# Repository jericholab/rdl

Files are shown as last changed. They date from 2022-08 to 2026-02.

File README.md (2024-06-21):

# Resistance Data Logger (RDL) by Jericho Lab

The RDL is an open-source suite of ready-to-use data logger and sensors designed for scientists and engineers.

The RDL is an open-source ready-to-use data logger designed for scientists and engineers.

For bugs and suggestions, users are invited to submit issues via Github.

Visit the official website: https://jericholab.com

**Purchase orders**  
Contact us via email or Linkedin.
 
**Licenses**  
SOFTWARE: GPL 3.0 license  
HARDWARE: MIT license  
WEBSITE & DOCUMENTS: Creative Commons CC-BY-NC-SA (Non-commercial use only)

For more information about the user permissions and responsibilities associated with each license, please refer to our website or contact us via email at info@jericholab.com. Thank you! 

<figure>
<p align="center">
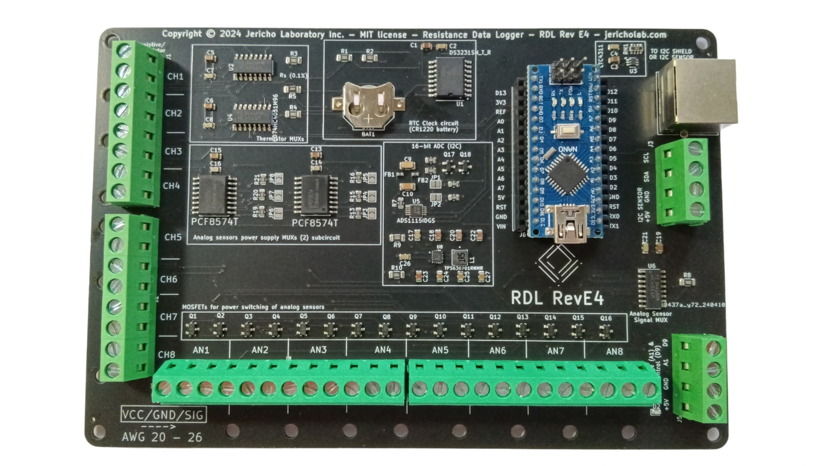
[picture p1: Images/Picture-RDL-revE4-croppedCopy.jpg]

  </p>
<p align="center">
RDL Data Logger revE4 with two I2C Shields
  </p>
</figure>

<figure>
<p align="center">
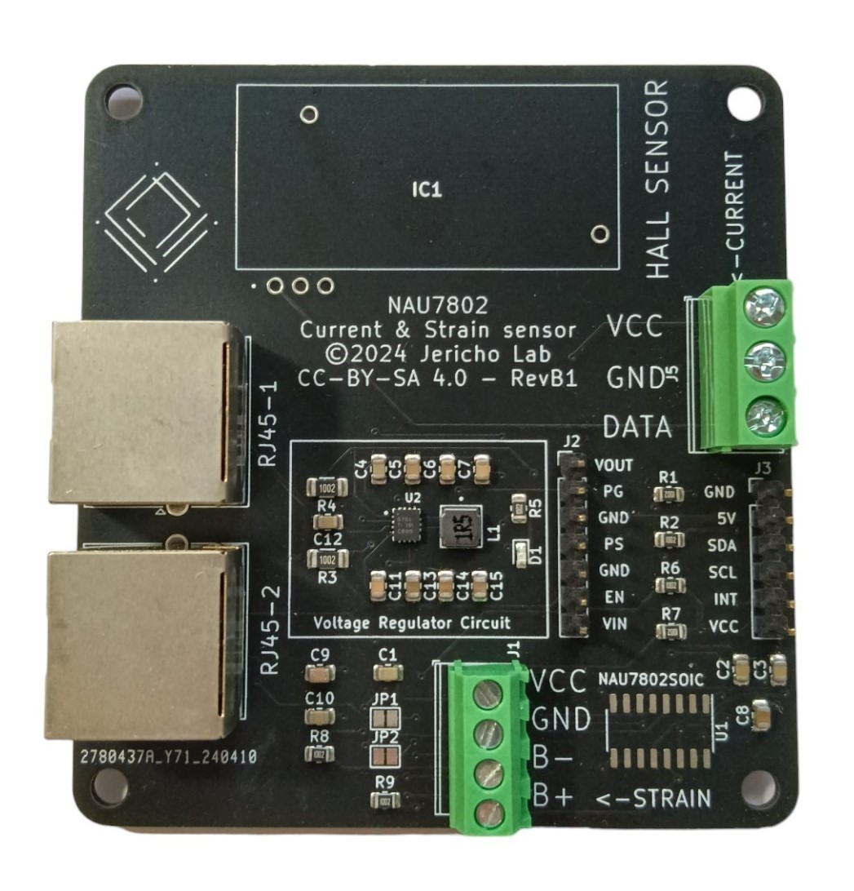
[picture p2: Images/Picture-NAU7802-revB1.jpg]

  </p>
<p align="center">
NAU7802 RevB1 for strain, force and current measurements
  </p>
</figure>

<figure>
<p align="center">
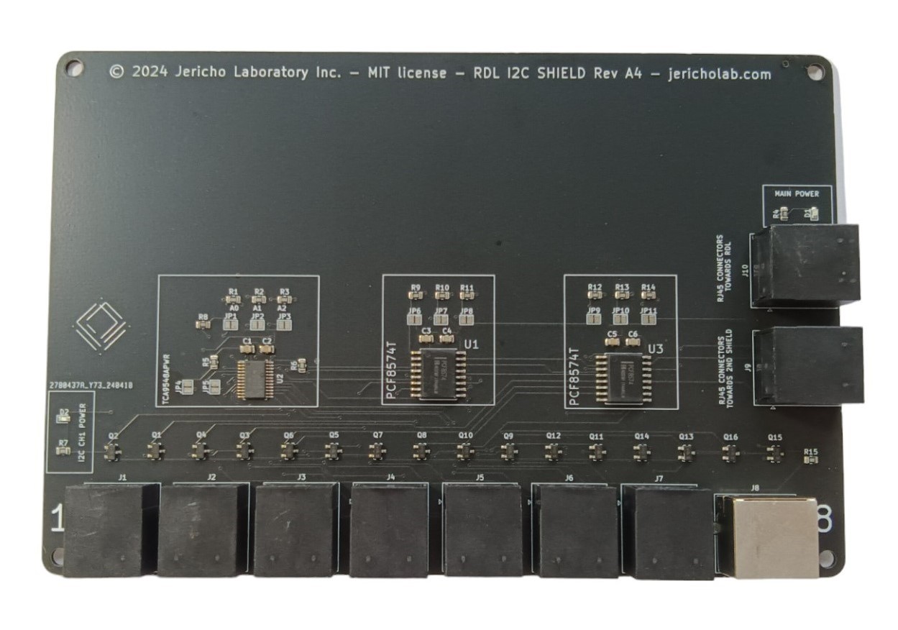
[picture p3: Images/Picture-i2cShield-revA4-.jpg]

  </p>
<p align="center">
RDL I2C Shield, revA4
  </p>
</figure>

<figure>
<p align="center">
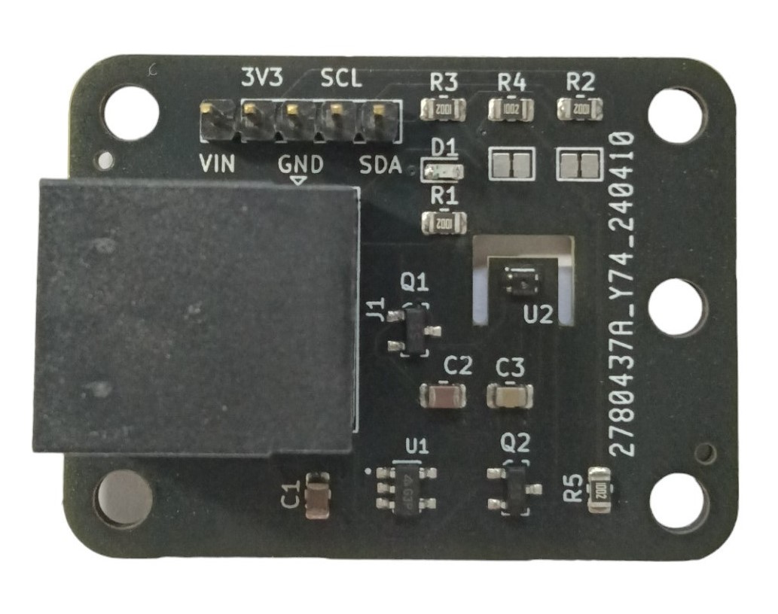
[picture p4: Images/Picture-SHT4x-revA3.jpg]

  </p>
<p align="center">
SHT4X revA4 for temperature and air humidity measurements
  </p>
</figure>

<figure>
<p align="center">
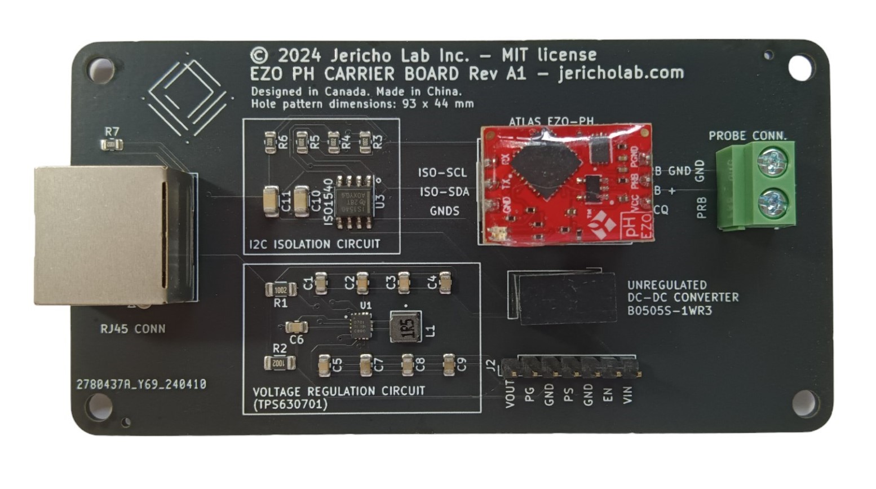
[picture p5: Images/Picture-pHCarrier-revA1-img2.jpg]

  </p>
<p align="center">
Carrier board for EZO PH (Atlas Scientific), revA1
  </p>
</figure>

<figure>
<p align="center">
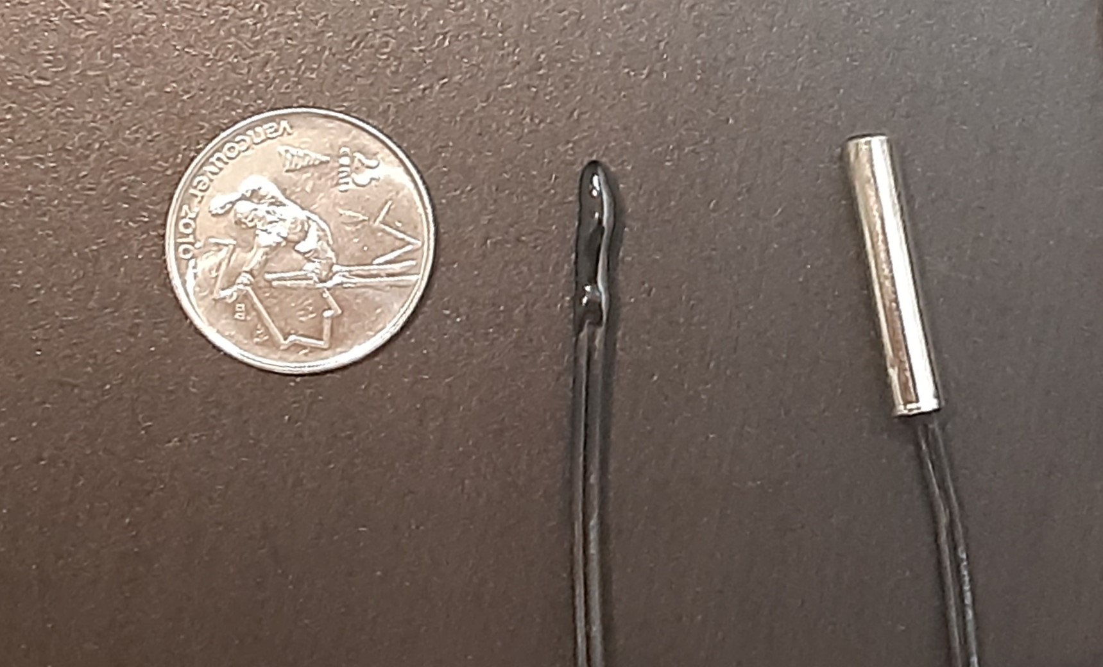
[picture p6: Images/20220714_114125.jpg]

  </p>
<p align="center">
NTC Thermistor probes TH-1 and TH-2 for temperature measurements
  </p>
</figure>

<figure>
<p align="center">
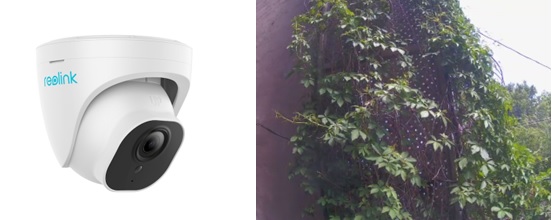
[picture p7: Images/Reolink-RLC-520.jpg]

  </p>
<p align="center">
 Python controlled Reolink RLC-520A Surveillance camera
  </p>
</figure>

<figure>
<p align="center">
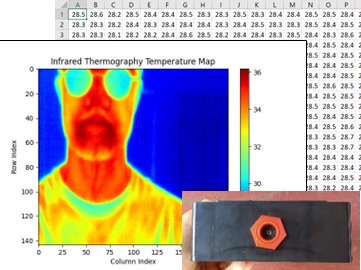
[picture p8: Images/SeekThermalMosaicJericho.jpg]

  </p>
<p align="center">
Outdoor radiographic camera based on Seek Thermal Mosaic Core
  </p>
</figure>

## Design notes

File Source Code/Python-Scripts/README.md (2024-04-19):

PYTHON SCRIPTS

The python scripts allow the integration of the surveillance camera, the infrared camera and the RDL Data Logger into the Orange Pi 4 LTS. The Python scripts can be run in various ways:
1) Run a single script within Thonny
2) Run all scripts by executing the shell script "WIRED-runAll.sh"
3) Run them via Daemons (next section)

DAEMONS

A shell script (.sh) will activate permanent services (daemons) via configuration files (.services) which run the usual python scripts (e.g. infrared.py).

1- Stop all the WIRED python scripts, if any were running.

2- Open a new terminal in the "/daemons-wired "folder, and execute  "$ sudo ./wired-enable-start-all-daemons.sh". This will copy a few files into the system, enable the daemons, start the scripts and show status.

3- You can verify the scripts are running by verifying the usual output (/logging-folder).

4- If you only want to verify that each python script is running, open a terminal in the "/daemons-wired "folder, and execute  "$ sudo ./wired-status-daemons.sh". Use page up and page down to look at all the lines.

5- Reboot the computer and verify the scripts are still running (since the daemons have been enable, they will start at boot time)

6- If you want to stop and disable all the scripts, execute  "$ sudo ./wired-disable-stop-all-daemons.sh"

7- If you wish to stop temporarily a given script (e.g. infrared camera), "$ systemctl stop infrared.service"  (It WILL restart at next OS reboot)

8- If you wish to stop permanently a given script (e.g. infrared camera), "$ systemctl disable infrared.service"  (It WILL NOT restart at next OS reboot)

Remember to keep the files associated with daemons in their own subfolder.

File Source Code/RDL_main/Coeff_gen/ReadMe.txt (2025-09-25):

1. Go to "Source Code/Coeff_gen/" and execute the RunMe.py script file. This will generate a header file (i.e. coefficients.h).
2. Copy coefficients.h to "../RDL_main/Coeff_gen/"
3. Compile RDL_main with the Arduino IDE compiler function.

END

the Jericho Lab team

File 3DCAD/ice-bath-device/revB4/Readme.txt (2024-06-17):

ice-bath-device-revB4

------ List of successful 3D Printing material
OVERTURE PETG Filament 1.75mm

------ 3D Printing Software version used 
Ultimaker Cura 5.2.1

------ Printing profile
N/A. As a starting point, the standard Jericho profile can be used (Profile-PETG-Bibo2-extruder-no2-2024-04-18.curaprofile).

------ 3D Printing Machine Used
Bibo 2

------ Reference to original design, if applicable 
Original design by Jericho Lab, copyright applies, open-source license CC-BY-NC-SA

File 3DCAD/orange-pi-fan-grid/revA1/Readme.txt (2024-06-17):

orange-pi-fan-grid-revA1

------ List of successful 3D Printing material
OVERTURE PETG Filament 1.75mm
PLA Filament 1.75mm

------ 3D Printing Software version used 
Ultimaker Cura 5.2.1

------ 3D Printing Machine Used
Bibo 2

------ Reference to original design, if applicable 
Original design by Jericho Lab, copyright applies, open-source license CC-BY-NC-SA

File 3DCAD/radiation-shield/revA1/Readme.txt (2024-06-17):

radiation-shield-adapter-revA1

------ Radiation shield adapter for the Jericho SHT4X board
Other parts of the Open Source Radiation Shield design included for reference only (Plates, topPlate,pipeSupport, SensorSupport)

------ List of successful 3D Printing material
OVERTURE PETG Filament 1.75mm

------ 3D Printing Software version used 
Ultimaker Cura 5.2.1

------ 3D Printing Machine Used
Bibo 2

------ Reference to original design, if applicable 
Original design by FAST Research group, available on appropedia.org.
https://www.appropedia.org/Design_and_Implementation_of_3-D_Printed_Radiation_Shields_for_Environmental_Sensors
Modifications by Jericho Lab, copyright applies, open-source license CC-BY-NC-SA

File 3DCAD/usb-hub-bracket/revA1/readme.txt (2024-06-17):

usb-hub-bracket-revA

------ Description
Allow the installation of USB hub to mounting panel. Design adapted model "Atolla Aluminum 4-in-1 USB Splitter with 1 USB 3.0 Port and 3 USB 2.0 Ports"

------ List of successful 3D Printing material
OVERTURE PETG Filament 1.75mm

------ 3D Printing Software version used 
Ultimaker Cura 5.2.1

------ 3D Printing Machine Used
Bibo 2

------ Reference to original design, if applicable 
Original design by Jericho Lab, copyright applies, open-source license CC-BY-NC-SA

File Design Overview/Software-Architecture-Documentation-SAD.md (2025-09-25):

**Software Architecture Documentation (SAD) for RDL**  
=======================================
Copyright: Jericho Laboratory Inc.  
Documentation license: CC-BY-SA.  

# Table of Contents

- [Introduction](#introduction)
- [High-Level Flow Diagram](#high-level-flow-diagram)
- [General Ideas](#general-ideas)
- [Fundamental Concepts](#fundamental-concepts)
- [Included Libraries](#included-libraries)
- [Main Code](#main-code)
  - [Declarations](#declarations)
  - [Setup()](#setup)
  - [Loop()](#loop)
- [Main Functions](#main-functions)
  - [ControlFunc()](#controlfunc)
  - [currentNAU7802()](#currentnau7802)
  - [initRTC()](#initrtc)
  - [phFunc()](#phfunc)
  - [printHeader()](#printheader)
  - [runRTC()](#runrtc)
  - [SHT40Func()](#sht40func)
  - [simpleVoltFunc()](#simplevoltfunc)
  - [startMessage()](#startmessage)
  - [strainFunc()](#strainfunc)
  - [terosFunc()](#terosfunc)
  - [thermistor()](#thermistor)
- [Support Functions](#support-functions)
  - [ADS1115.begin()](#ads1115begin)
  - [blink()](#blink)
  - [calculatePhi()](#calculatephi)
  - [commands()](#commands)
  - [getI2Cfreq()](#geti2cfreq)
  - [getVoltFunc()](#getvoltfunc)
  - [i2cScan()](#i2cscan)
  - [I2CSelect()](#i2cselect)
  - [isDST()](#isdst)
  - [pcf1.begin()](#pcf1begin)
  - [readEEPROM()](#readeeprom)
  - [resetFunc()](#resetfunc)
  - [setMultiplexer()](#setmultiplexer)
  - [setTime()](#settime)
  - [spacing1()](#spacing1)
  - [spacing2()](#spacing2)
  - [tca_init()](#tca_init)
  - [tca_select()](#tca_select)
  - [watchSerial()](#watchserial)
- [Standard Functions](#standard-functions)
- [Useful References](#useful-references)

# INTRODUCTION

- The Software Architecture Document (SAD) is a good practice for any software project. It is used to guide developers and maintainers in understanding and working with the software. It provides a comprehensive blueprint of the software structure, which is essential for effective maintenance and scalability of the software over time. The SAD also covers the software development practices, coding standards, and software deployment process. It serves as a reference that captures the rationale behind certain architectural decisions, which might not be immediately apparent from the code itself. Over time, as the collaborators change, having a documented architecture can ensure that the understanding of the system's design persists.
- The document tries to introduce some of the fundamental coding concepts, but it is not exhaustive. It is no substitute to reading the source code, which is heavily commented.
- In the future, the RDL SAD will be converted to the arc42 open-source template. The document might also evolve to a _System_ Architecture Documentation and include hardware architecture. For example, the present document does not include conventions about the products schematics and circuit layouts.
- The present document refers to the last available version of the main code for the latest hardware revision.
- This document is complementary with the Design Overview documents, which focus mostly on the hardware design and overall functionality. The Design Overview latest files are located in the main branch of the Jericho Git Hub repository and include the following files:
  - Design Overview - General Information.md
  - Design Overview - Atmospheric Humidity Sensor.md
  - Design Overview - Resistance Data Logger Revision E4.md
  - Design Overview - IP Camera System.md
  - Design Overview - NAU7802 Strain Current Sensor.md
  - Design Overview - Hall Effect Current Sensor.md
  - Design Overview - I2C Shield.md
  - Design Overview - pH Meter.md
  - Design Overview - Thermal Camera.md
  - Design Overview - WIRED Main Hub.md
  - Design Overview - WIRED Daemons.md
  - Design Overview - WIRED Infrared CSV.md
  - Design Overview - WIRED Python Script RDL.md
  - Design Overview - WIRED Reolink.md
  - Design Overview - WIRED Syncing.md

# HIGH-LEVEL FLOW DIAGRAM

<figure>
<p align="center">
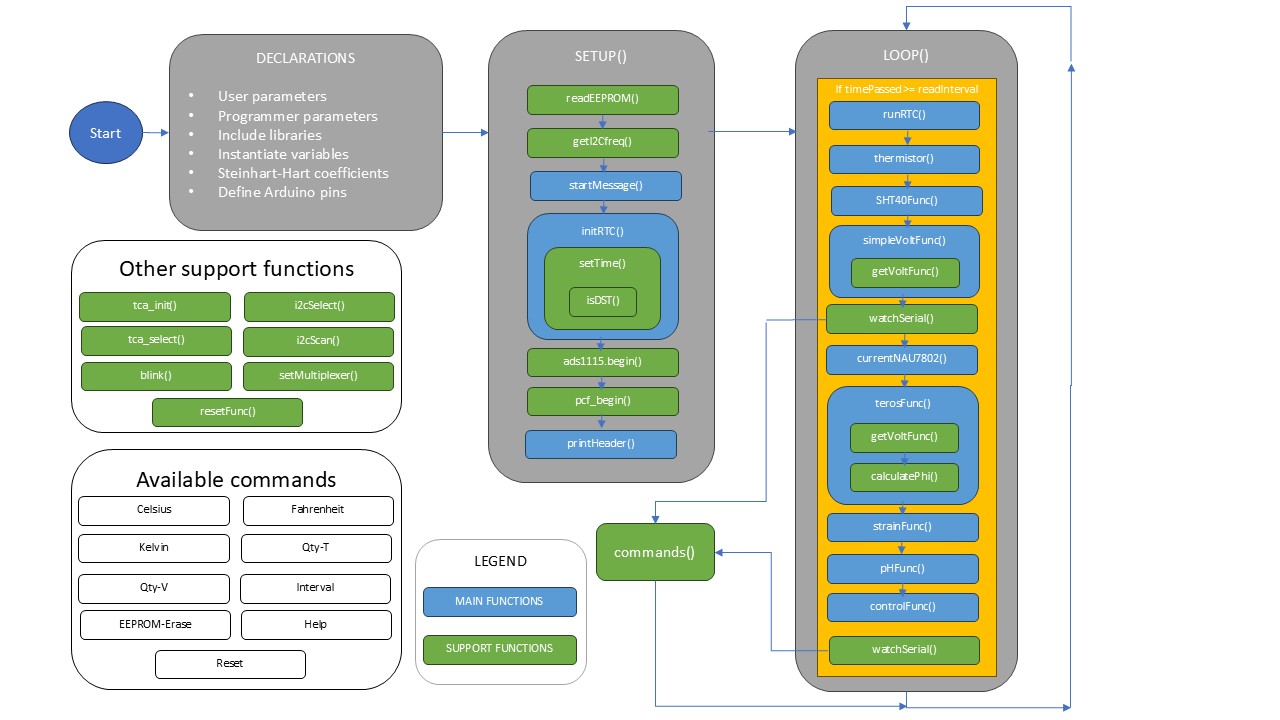
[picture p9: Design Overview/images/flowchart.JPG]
  
    </p>
</figure>
<p align="center"> High-level flow diagram of the RDL system

# GENERAL IDEAS

- **Dataflow**: At regular interval, the RDL asks, one by one, each analog/digital sensor to provide data. The RDL collects the data and transmits it to the PC (e.g. Raspberry Pi) via an emulated Serial connection. The PC captures the incoming data from the RDL. RDL dataflow is entirely controlled by the RDL.
- **Simplicity**: The RDL coding style priorities simplicity over efficiency. This allows a greater number of users to understand and modify the code. The code is highly commented and avoids jargon, when possible, for that same purpose. Simplicity will also help early-stage AI agents grasp code more easily, as users progressively transfer coding tasks to AI tools.
- **Measurement printing:** A measurement is only made if displayed, and only displayed if made. This maximizes the measurement speed. Therefore, a single parameter is required to decide on both.
- **Parameters**: Some parameter values can be changed while using the product (e.g. acquisition interval), while others can only be changed in the source code (.ino), before compilation and upload via USB cable (e.g. type of sensors activated).
- **Language**: The programming language is C, with the use of some C/C++ libraries. The use of a procedural language (i.e. C) is deemed simpler than integrating object-oriented language (i.e. C++) into the code. Since the average user is not expected to modify the libraries, the use of C++ libraries does not increase the complexity.
- **Segmentation**: The code is divided into different files which appear as different tabs inside the Arduino IDE.
- **IDE**: We recommend using the Arduino IDE software to read and edit the source code. Since this is the most common popular IDE in the Arduino community, the code was made as compatible as possible with the Arduino IDE. More advanced user can use Visual Studio (PlatformIO), Sublime and other IDEs.
- **Memory use**: Jericho maintains the production code at a maximum of 75% of the Arduino memory. For the ATMega328p, the memory capacity is 32KB (flash), 2KB (volatile memory), 1K (EEPROM, non-volatile memory). It is possible that the user runs out of memory (flash or volatile) when adding functionalities to the RDL. Adding instances of a given sensor also increases memory usage. To solve this problem, the user has some options: 1) Use an Arduino Nano Every instead of an Arduino Nano V3, thereby increasing by 50% the available Flash memory and tripling the SRAM; 2) delete/deactivate unused functions from the code; or 3) add another RDL to the experiment.
- **Github**: The code is stored on GitHub public account of Jericho.
- **Versions**: The date is not included in the source code filename to avoid confusion with GitHub versioning. However, to easily identify the version currently running on your RDL device, the compile timestamp is printed out to the Serial Monitor at boot time. This can give you a clue that you might be running a rather old version of the firmware.
- **Memory optimization**: Multiple methods and conventions are used consistently throughout the code to reduce flash memory use (e.g. use #define, use char arrays instead of String) and SRAM memory use (e.g. send variable to flash memory). Developers must apply those techniques for their pull requests.
- **I2C extender**: The I2C extender (LTC4311) boosts the I2C bus voltage every time it detects a rising edge. This was intended to help preserve the I2C signal shape on buses with high capacitance (impedance). A low-cost oscilloscope (starting from \$60 on Amazon) can be used to evaluate the signal shape in a given setup.
  - ⚠️ **UPDATE:** Testing revealed that the LTC4311 I²C extender often degrades performance when used in combination with the I²C shield and long cables (>5 m). The root cause appears to be impedance mismatch: the LTC4311 sharpens signal edges, which leads to reflections and ringing at the transition between the shield's narrow PCB traces and the external cables. This results in communication instability or corruption.
  - Therefore, **it is recommended to deactivate all LTC4311 chips** by manually cutting the power supply trace (delicate and risky operation). This chip will likely be removed from the next RDL board revision.
- **Analog sensors**: Two types of analog sensors are natively supported by the RDL platform: resistive and analog voltages (0-5V). Each category has a dedicated section of screw terminals. The analog voltage sensor must be referenced to the same ground than the RDL. This is why the terminals provide mandatory VCC, GND and SIG pins.
- **Product evolution**: Ideas and pull requests from users will be accepted on the basis of the first principles attached to the project, as well as the mission and philosophy of the company.
- **ADC Reference**: For the Nano ADC, the 3.3V regulator is used because it produces a cleaner signal (lower level of electromagnetic noise) than the 5V bus from the USB cable (unregulated). The 3.3V bus also has fewer electronic components connected to it. This cleaner signal helps provide a more stable reading of the thermistor probes.
- **EEPROM-Initialization**: This tiny program can be found on our Github and erases the EEPROM. When the main program is subsequently re-uploaded, in the absence of any values on the EEPROM memory, it will use default values found in the Flash memory. This separate Arduino program can be necessary in some rare cases where the EEPROM parameters create such a weird RDL behavior, that the command "EEPROM-ERASE" from the main program cannot be sent or executed successfully.

# FUNDAMENTAL CONCEPTS

- **Bootloader**
  - The bootloader is a tiny program that initializes communication with the microprocessor.
- **Library**
  - A library is a piece of code that has pre-made functionalities. Like any code, a library will take memory space. The library must be installed to the Arduino IDE before being added (#included) to the code.
  - Including a library with #include will make it known to the Arduino IDE compiler, but only the parts of the library that are actually used (referred to in your code) will likely end up in the final executable - and occupy memory space. This is because most modern linkers perform a process called "link-time optimization" or "dead code elimination" where unused code is not included in the final binary.
- **Serial Communication**
  - The Nano CPU emulates a serial communication between the microcontroller and the computer. All data that is transmitted by the RDL is numerical data. Therefore, data might be lost due to noise or else, but the accuracy is not dependent on the cable used or the receiving end (i.e. computer).
- **Local and global variables**
  - A global variable exists throughout the code. It can be seen by every function. A local variable is created inside a given function and is destroyed when exiting the function. It cannot be seen by functions outside the given function.
- **Memory (flash):** Flash memory on an Arduino Nano is non-volatile storage used to hold the device's program code and is retained even when the power is turned off.
- **Memory (volatile):** Volatile memory, commonly referred to as SRAM (Static Random Access Memory) on an Arduino Nano, is used for temporary data storage while the program is running and is lost when the device is powered down or reset.
- **Memory (EEPROM)**: EEPROM (Electrically Erasable Programmable Read-Only Memory) on an Arduino Nano is a form of non-volatile memory used to store small amounts of data that must be saved between sessions, like configuration parameters, that can be read and written during runtime.
- **ADC (Analog-to-digital converter):** This device converts analog signal (voltage potential) into a numerical signal (bits). The quality of the ADC is one of the factors that limits the best accuracy obtainable with a data logger. The Arduino Nano uses a 10-bit ADC. This means that it can translate its voltage range (ex: 0-3.3V) from bit 0 to 1023 (2^10). The ADS1115 is a 16-bit ADC that translates its voltage from bit 0 to 65535 (2^16). This is 64-fold increase in conversion accuracy. Measurements that use the getVoltFunc() have the ADC selection as function input (readMode 1 = ADS1115, readMode = 0 for Nano ADC).
- **Variable types:** A number of common variable types are found in the code. Here are short definitions in the context of 8-bit microcontrollers, like Nano's ATMega328p. The variable types are important since 1) they might have incompatibilities with the certain logical or mathematical operations and 2) might cause waste of memory resources.
  - **char**: A char stores a single byte of data, which can represent a single character in the ASCII encoding scheme. It is typically used to store characters like 'a' or '\$', or control characters like '\\n' (newline).
  - **int**: On the Arduino platform, an integer (int) stores a 16-bit (2-byte) value. This means it can store values between -32,768 and 32,767.
  - **long**: A long stores a 32-bit (4-byte) value. Thus, it can contain values from -2,147,483,648 to 2,147,483,647.
  - **unsigned long**: An unsigned long is a 32-bit (4-byte) value that can hold integers from 0 to 4,294,967,295.
  - **String (upper case 'S')**: This is an object type provided by the Arduino library, representing a string of characters, but with overhead due to dynamic memory allocation and the methods it provides.
  - **string (lower case 's')**: In Arduino programming, the term string typically refers to an array of characters that is used to store text. This is the traditional C-style string, which is a sequence of characters terminated with a null character (\\0). It is a lower-level way of handling strings compared to the String class, and it is generally more memory-efficient, which is appreciated in a resource-constrained environment like the Arduino.
  - **uint8_t**: An unsigned 8-bit integer (1-byte), capable of storing values between 0 and 255. It is often used for raw binary data, byte-level operations, and optimizing memory usage.
  - **float**: On the Arduino, a float is a 32-bit (4-byte) value with a precision of approximately 6-7 decimal digits. It represents a single-precision floating-point number.
  - **struct**: A composite data type that allows grouping of variables of potentially different types under one name, useful for representing complex data structures.
  - **#define**: This is a preprocessor directive, not a variable. It tells the compiler to replace all instances of the defined identifier in the code with the provided value or code snippet, before the actual compilation process begins. This operation happens at compile time.

# INCLUDED LIBRARIES

All libraries below are open-source and can be installed from the Arduino IDE Library Manager or it can be copied from

\\Jericho-github-repo\\rdl\\Source Code\\Arduino-libraries\\libraries  
to  
\\Arduino\\libraries.

An advanced user could remove some libraries to potentially save some memory if he does not plan on using the associated functions.

- EEPROM.h
- RTClib.h
- Wire.h (modified version, 490 Hz instead of 100 kHz)
- Adafruit_SHT4x.h
- Adafruit_ADS1X15.h
- Adafruit_PCF8574.h
- Adafruit_SleepyDog.h
- Jericho_Adafruit_NAU7802.h
- Coeff_gen/coefficients_current.h
- Coeff_gen/current_coefficients.h
- MemoryFree.h

# MAIN CODE

The main code is a separate file which contains the declarations, the setup() and loop() functions.

## DECLARATIONS

- - A number of parameters are declared in the first section of the program, before and outside the setup() and loop() functions. These are global variables.
    - User parameters, include but are not limited to:
      - Activation of each sensor type (e.g. only measure and print strain sensors)
      - Activation of the custom control signal function.
      - Activation of the noise control mechanism.
      - Activate the optional printing of the resistance values.
    - Programmer parameters, include but are not limited to:
      - Establish the reading interval
        - The reading interval applies to all active sensors, without exception.
        - The measurement interval parameter is a target only; it is not enforced. If there are too many operations to be made, the cycle will run but take longer than expected. This strategy ensures that the program will run even if the interval chosen is not realistic given the quantity of sensors selected. The user must always verify the data timestamps to ensure that the target interval is being respected.
      - Establish the default temperature units
      - Temporarily define which channels has which type of sensor (e.g. #define TEROS_PIN A1)
      - Libraries to be included
      - Indicate the series resistor value
      - Provide the Steinhart-Hart coefficients values
      - Create instances of some libraries (e.g. RTC_DS3231 rtc; )
      - Define measurement samples size.

## SETUP()

- - This function exists in every Arduino code.
    - It runs once after any power up or reset of the controller via the reset button or the reset command.
    - Initializes the serial monitor and prints some general information for the benefit of the user.
    - Tells the microcontroller unit to use the external voltage as a reference for the Analog to Digital converter (ADC). In the present case, this voltage is the 3.3V DC signal generated by the Arduino.

## LOOP()

- - This function exists in every Arduino code.
    - This function is continuously repeated as long as the end is reached.
    - Update timers.
    - Take the decision to read the probes if enough time has passed.
    - Listen to the Serial monitor for incoming commands.

# MAIN FUNCTIONS

The measurement functions do the core job of communicating with sensors and producing measurements.

## ControlFunc()

- - This function is a simple example of a control signal that can be generated by the RDL. In the provided example, if voltage for channel 0 is higher than voltage for channel 1 a non-regulated 5V signal is produced at pin D9.

## currentNAU7802()

- - Measures electrical current from a TAMURA Hall-effect sensor (model L01Z050S05) using the NAU7802 24-bit ADC module (normally used for strain gauges). It currently supports DC current only.
    - Initialization & sensor check
      - If the current sensor hasn't been set up yet, it calls beginCurrent() to initialize it.
      - Marks the sensor as present if initialization succeeds.
    - Sensor configuration
      - Enables the NAU7802, sets the sample rate (10 samples/sec), powers it via an external LDO, and runs an internal calibration.
    - Data collection with outlier rejection
      - Reads multiple ADC samples (n=2 by default, but can be larger).
      - For each pair of consecutive reads, it discards any pair with a difference greater than 5000 ADC counts.
      - Averages the accepted readings.
    - Temperature compensation (optional)
      - If currentTComp is enabled, adjusts the offset based on the measured temperature (T_comp) and a known temperature drift slope.
    - Voltage-to-current conversion
      - Converts averaged ADC counts to volts using a predefined slope and offset.
      - Subtracts a calibrated zero-load voltage (zeroValue), applies temperature drift correction, and multiplies by the Hall sensor ratio (A/V) to get amps.
    - Output values
      - Sensor temperature.
      - Temperature offset drift.
      - Last valid raw ADC reading.
      - Calculated sensor voltage.
      - Final calculated current (amps).

## initRTC()

- - Initialize the real-time clock.

## phFunc()

- - Reads the pH sensor that has been selected by the I2C multiplexer function.
    - There is a 2 minutes warm-up delay after powering up the pH sensor in the main loop, before entering the pHFunc per say, and reading the pH probe. This delay is especially essential for industrial-grade pH probe membranes, which are less porous and take more time to reach chemico-electrical equilibrium. Lab-grade probes could stabilize faster.
    - Prints out the sensor value with 3 decimals precision.
    - For more information about the probe calibration, please refer to the pH meter design overview.

## printHeader()

- - Displays the column headers for the sensor data log, based on which sensor types are currently active.
    - This function dynamically prints a title row to the serial monitor, adapting the header to match the configuration of the connected sensors (e.g., temperature, resistance, SHT40, voltage, current, Teros, strain, pH). Each active sensor type is checked via a corresponding display flag (e.g., tDisplay, ohmDisplay, etc.), and only the relevant headers are printed.
    - The formatting aligns each column with consistent spacing using the spacing2() function. This ensures proper visual alignment of sensor readings during serial output. Headers are also prefixed with markers (\*, #, etc.) for readability or parsing purposes.
    - ⚠️ The function is highly modular and assumes global flags (xDisplay) and sensor counts (qty_xx) are set appropriately before calling.

## runRTC()

- - Ask the Real-Time Clock (RTC) chip to provide the current time (standard time, no DST).
    - This data is directly printed out by the function.

## SHT40Func()

- - Checks if the SHT40 humidity/temperature sensor should be displayed and, if not yet detected, attempts initialization. Marks the sensor as present if successful.
    - Sets measurement precision to high (slower but more accurate).
    - On the first run, activates the medium heater for 1 second to remove possible condensation, prints an ampersand (&) to indicate this heating, and disables heating in subsequent runs.
    - If the sensor is present, reads temperature (°C) and relative humidity (%RH) and prints them with formatted spacing; otherwise, prints zeros.

## simpleVoltFunc()

- - This function controls the multiplexer and calls getVoltFunc() the required number of times. The output is in volts.
    - The number of measurements is controlled by QTY-V.

Measurements are always done from channel 1 and onward. This means that if channel 5 is of interest, channel 1 to 5 must be measured and printed.

## startMessage()

Print out the initial message at startup with information like temperature units, reading interval, compile date, thermistor wire resistances considered. It also prints the optional header (i.e. printHeader()).

## strainFunc()

- - The function reads data from a single specific strain sensor (i.e. load cell) connected to the system. The function name, "strain", is a misnomer; the function actually measures force and moment, from which strain values can be calculated by the user during post-treatment.
    - Initializes the NAU7802 load-cell ADC once per channel; marks the strain sensor present and increments an initialization counter when begin() succeeds. Once the counter value is equal to the number of sensors connected to the system, we assume that all NAU7802 chips have been initiated and the initialization is skipped until the next RDL reboot.
    - If present, powers the ADC on, flushes the first 10 samples (waiting for available() each time), then reads a raw ADC value.
    - Computes force \[N\] using the per-sensor calibration slope a and offset b, which are stored in the coefficients.h library (Flash memory). It also computes moment \[N·m\] using the 40 mm gauge spacing.
    - Prints the raw ADC reading (integer-formatted), the computed force, and the computed bending moment, with fixed spacing for aligned columns.
    - Powers the ADC off after the measurement to allow clean power-cycling on the next run.
    - If the sensor is not present, prints zeros for ADC, force, and moment.
    - How the main code calls it (per-channel loop)
      - Iterates over all strain channels; for each, selects the TCA9548A I²C channel, wraps the call with Wire.beginTransmission()/Wire.endTransmission(), and passes that channel's calibration coefficients from strain_matrix\[i\]\[0..1\] into strainFunc(a,b).
      - Turns on/off the sensor via pcf3/pcf4, inserts short delays to avoid bus glitches, and re-initializes the mux with tca_init() after each reading to prevent I²C bus jams.
    - In future developments, to save space on the Flash, strain coefficients could be uploaded to EEPROM memory.
    - For more information about the calibration process, consult the "NAU7802 Strain Current Sensor" Design Overview.

## terosFunc()

- - Reads the TEROS 10 analog sensor that has been selected by the multiplexer function.

Prints out the sensor value in relevant units (Pa, m<sup>3</sup>/m<sup>3</sup>).

## thermistor()

- - Reads a single thermistor probe sensor that has been selected by the multiplexer function.
    - The function inputs are: the channel number, the read mode, and the Steinhart coefficients (A, B, C).
    - If readMode ==0, the Nano ADC is used. If readMode == 1, the ADS1115 ADC is used instead (more accurate).
    - The function returns two outputs in a single structure: the resistance value (Ω) and the temperature value (C/F/K). The function does not print anything to the Serial Terminal.
    - For the coefficients, ten (10) decimals must be entered into the program in order to obtain the nominal accuracy of the device.
    - Some parameter values are stored in the EEPROM (i.e. temperature units, reading interval, QTY-T, QTY-V). The serial command will update the value stored and therefore, after restart, the value is retained.
    - Each thermistor probe has a slightly different temperature-resistance relationship. However, contrarily to early versions of the RDL, there are no custom Steinhart-Hart coefficients. The individual probe calibration process is now used to exclude probes outside the system-level accuracy target (i.e. +/- 0.5°C) (see GNU Octave analysis) . This greatly simplifies the user experience by avoiding the frequent manipulation of 10-decimals probe coefficients, and allowing the interchangeability of probes.
    - The thermistor function takes into account the internal electrical resistance (70 ohms) of the two multiplexers in order to accurately predict the temperature.
    - Beside non-linearity, the thermistor's main weakness is self-heating. This is because current goes through the highly resistive component in order to measure it, causing heat generation via the Joule effect. This effect is largely minimized by measuring the value a small fraction of time. The thermistor multiplexers are only enabled (via a dedicated pin) for the short period where the reading occurs. This beneficial strategy is reduced when doing high-frequency measurements, where a higher fraction of time is under tension. If making 400 measurements per second, this Joule effect becomes noticeable again. The nominal accuracy is calculated for a 1 second measurement interval. The Joule effect is less in water (high specific thermal capacity value) compared with air.
    - In a similar way, the cable resistance must be calculated and added to the code. Otherwise, the error will increase with wire length and gauge number.

# SUPPORT FUNCTIONS

The support functions are those functions doing support tasks for the measurements and control functions. They are presented here in alphabetical order.

## ADS1115.begin()

- - Native function from the ADS1115 library (by Adafruit) to initialize the 16-bit ADC chip for high-accuracy measurements.

## blink()

- - This function is used to blink the LED on the Arduino Board. This function is used to signal some activities to the user.

## calculatePhi()

- - Returns the soil water tension (matric potential) in \[Pa\], computed from the volumetric water content (VWC) input (in \[m³/m³\]) as measured by the analog sensor (i.e. TEROS 10).
    - Soil water tension represents the mechanical energy a plant must exert to extract water from the soil. The lower the soil water content, the higher the mechanical energy required to extract water from the soil. Other factors, such as soil composition, also influence the energy requirement. This relationship between water content and tension is modeled using the common van Genuchten semi-empirical equation, which approximates the soil water retention curve.
    - ⚠️ Note: The current implementation uses a generic sample curve, not calibrated to local soil properties. Therefore, it should not be used for field operations without soil-specific parameterization.

## commands()

- - commands() is a function called by watchSerial(). If the Serial Monitor has received a non-empty string, the commands() function runs the appropriate command based on the incoming text.
    - If the RDL has 20 sensors, once it starts to read the 20 sensors, no command will be able to interrupt the read sequence until it ends, which can take over 10 to 60 seconds. This is why the program verifies any incoming command with watchSerial() at multiple points through the loop().
    - The function contains multiple pseudo-functions (code snippets activated by if() statements):
      - Celsius (Use Celsius as temperature units)
      - Fahrenheit (Use Fahrenheit as temperature units)
      - Kelvin (Use Kelvin as temperature units)
      - Qty-T (Update the number of temperature probes active)
      - Qty-V (Update the number of analog sensors (voltages) active)
      - Interval (Update the time interval for periodic measurements)
      - EEPROM-Erase (Erase the EEPROM, forcing the use of default settings)
      - Help (Print out the available commands)
      - Reset (Reset the microcontroller)

## getI2Cfreq()

- - The RDL operates its I2C bus at an abnormally low clock frequency: 489Hz instead of 100,000Hz. It allows the I2C protocol to operate effectively on very long cables (i.e. 30m). More information can be found in the source code (i.e. twi_readme.txt).
    - The getI2Cfreq() function allows the user to confirm that the I2C bus is truly operating at the expected frequency for long cable communication.
    - The function reads the hardware register values (e.g. TWSR, TWBR) and preprocessor macros (e.g. F_CPU) defined by AVR/io.h to calculate the effective I2C bus frequency and return the result to startMessage() for print out.

## getVoltFunc()

- - This function is called by the simpleVoltFunc() for voltage measurements and also the terosFunc for soil moisture measurements.
    - getVoltFunc() only makes the actual measurement. It does not print out anything.
    - Depending on the selected option, the function will either use the ADS1115 chip or the Nano ADC to make a measurement.

## i2cScan()

- - This function scans the I2C bus for all connected devices, including those on the main I2C bus and any multiplexed sensors attached to the TCA9548 multiplexer. It helps in detecting both the RTC chip and other I2C devices connected to the system.
    - Trigger: The function is executed when the I2CSCAN command is sent via the Serial Monitor. It is called by the commands() function.
    - Multiplexer Handling: The function begins by selecting each I2C channel of the TCA9548 multiplexer one at a time using the tcaselect() function, ensuring that only one channel is active during each scan.
    - Address Scanning: It scans all 128 possible I2C addresses (from 0x00 to 0x7F). The scan skips the address of the multiplexer (TCAADDR) to avoid detecting the multiplexer itself.
    - Device Detection: For each address, the function attempts to communicate using Wire.beginTransmission(addr) and checks for acknowledgment with Wire.endTransmission(). If a response is received, the device at that address is considered active.
    - Output: The detected I2C devices are printed in the Serial Monitor, with the format Found I2C 0xXX, where 0xXX is the address of the device. The output will include any devices connected via the multiplexer (e.g., sensor modules like the ADS1115, PCF8574, etc.) as well as the RTC (DS3231).
    - Limitation: Since the function does not filter out duplicate devices, devices on the full bus, including the RTC chip, may appear multiple times (one for each active multiplexer channel). For example, the RTC might show up multiple times if it is connected to different multiplexer channels.
    - Future Development:
      - Multi-Shield Support: The function may be enhanced to support multiple I2C shields.
      - Duplicate Filtering: Future improvements could include preventing the printing of duplicate devices and refining the output to print devices only once, regardless of the multiplexer channel.
      - Instance Generation: Another potential future feature would be to automatically generate instances for sensors found during the scan.
      - Enhanced Output: Sensor names (e.g., EZO-PH, NAU7802) might be printed alongside their addresses for better clarity in future updates.

## I2CSelect()

- - Allows to select which i2c sensor the Nano communicates with by controlling the TCA9548 multiplexer channel.

## isDST()

- - Determines if the current date falls within the Daylight Saving Time period, as defined in Canada and USA. The function assumes the input (local compile time, "DateTime dt") is already localized. There is no detection of time zone, location, or offset. It also approximates that DST starts at midnight, not 2:00AM.
    - Returns true if we are within the Daylight-Saving Time period, otherwise returns false.

## pcf1.begin()

- - Initializes the PCF8574 I²C GPIO expander using the Adafruit PCF8574 library. This is a native method provided by the library and must be called before interacting with the chip. In this setup, multiple instances of the PCF8574 class are used (e.g., pcf1, pcf2, pcf3, pcf4), each assigned a unique I²C address (0x20, 0x21, etc.). These PCF chips are responsible for switching MOSFETs that control power supply lines: 1) Analog sensor supply (VCC, GND), 2) Digital sensor supply on the I²C shield (VCC, GND). Each PCF device acts as a remote I/O controller, enabling or disabling sensor power through its GPIO outputs.

## readEEPROM()

- - Read the EEPROM memory in search of stored parameters to be retrieved.
    - The table below lists the EEPROM addresses used in the RDL code revE2.
    - If the readEEPROM() function cannot find values for any of these variables, it will use default values. Addresses go from 0 to 1000, since the EEPROM is 1 kB. When you access an EEPROM address, you are reading or writing one byte (8 bits) of data.

| EEPROM ADDRESS | VARIABLE NAME | MEANING | VARIABLE TYPE | SIZE (BYTES) |
| --- | --- | --- | --- | --- |
| 0   | units_T | Temperature units | uint8_t | 1   |
| 4   | readInterval | reading interval | long | 4   |
| 8   | numberC_ROM | Number of channels | uint8_t | 1   |
| 9   | numberV_ROM | Number of channels | uint8_t | 1   |
| 100 | ohmDisplay_ROM | Display Resistance Values | bool | 1   |

## resetFunc()

- - Tiny one-line function that allows a software reset of the Nano without using the physical reset button. By asking the Nano to read the byte 0, it effectively resets the MCU.

## setMultiplexer()

- - Selects the desired input channel (0-7) on a single CD74HC4051 analog multiplexer by setting the appropriate logic levels on the three select pins (S0, S1, S2).
        - Input: channel (integer from 0 to 7)
        - Effect: Routes the chosen input channel of the CD74 multiplexer to the common output (e.g., for sensor reading).
    - Note: This function assumes the ENABLE pin is already active (LOW) and does not activate or disable the multiplexer.

## setTime()

- - Sets the RTC (Real-Time Clock) to the last compile time of the code. This time is used as the base timestamp for logged data.
    - By default, the function applies the non-DST (standard) time, regardless of the compiling computer's time zone or daylight saving setting. To correct for this, the function calls isDST() to check whether the current date falls within the Daylight Saving Time period, and also checks whether the user has indicated that DST is used in the local area.
    - If both conditions are true, the function subtracts 1 hour from the compile time before writing it to the RTC, effectively reverting to standard time.

## spacing1()

- - Tiny function used to add the right number of spaces to keep the columns straight in the Serial Monitor window. Spacing1() concerns the numbers, while spacing2() concerns text.

## spacing2()

- - Tiny function used to add the right number of spaces to keep the columns straight in the Serial Monitor window. Spacing1() concerns the numbers, while spacing2() concerns text.

## tca_init()

- - Initializes the TCA9548A I²C multiplexer located on the optional I2C shield.
    - The TCA9548A is an I²C multiplexer that enables the Arduino microcontroller to communicate with up to 8 separate I²C buses (SDA/SCL pairs), allowing multiple devices with identical I²C addresses to coexist on a single system. Each of the 8 channels can be activated individually to route communication to the desired device.
    - Upon power-up, the internal state of the TCA9548A is undefined, meaning one or more channels could be unintentionally active. This function ensures a clean and deterministic startup by writing 0b00000000 to the control register, thereby disabling all channels.
    - This prevents:
      - Bus contention between devices with shared addresses
      - Noise from floating or uninitialized I²C lines
      - Unintended communication with downstream sensors
    - For more implementation details, refer to the I2C Shield Design Overview document.

## tca_select()

- - Selects a specific channel (0-7) on the TCA9548A I²C multiplexer, allowing communication with one sensor on that channel.
    - The function writes a bitmask to the TCA control register using 1 << i, which shifts a 1 to the bit corresponding to the desired channel. For example:
      - i = 0 → 0b00000001 → enables channel 0
      - i = 3 → 0b00001000 → enables channel 3
    - All other channels are disabled.
    - If i > 7, the function exits without doing anything.

## watchSerial()

- - Small function called at every loop to monitor any potential incoming command from the Serial Monitor.

# STANDARD FUNCTIONS

Here below is a non-exhaustive list of standard functions used by the RDL code. These functions are part of the Arduino native environment or the standard libraries included. More details about these standard functions can be found on the official Arduino website.

- analogRead()
- analogReference()
- delay()
- digitalWrite()
- EEPROM.read()
- EEPROM.write()
- millis()
- pinMode()
- RTC_DS3231()
- Serial.begin()
- Wire.begin()
- Wire.beginTransmission()
- Wire.endTransmission()
- Wire.requestFrom()
- Wire.read()
- Wire.setWireTimeout()
- Wire.write()

# USEFUL REFERENCES

Arduino. (n.d.). Language reference. Retrieved August 8, 2025, from <https://www.arduino.cc/reference>

Working Software. (n.d.). Software architecture documentation: The ultimate guide. Retrieved August 8, 2025, from <https://www.workingsoftware.dev/software-architecture-documentation-the-ultimate-guide/>

Coulombe, F. (2025, August). Annex: Temperature measurements Accuracy [White paper]. Jericho Labs. https://github.com/jericho-lab/rdl

Coulombe, F. (2025, August 31). Octave code for Jericho [Computer code]. GitHub. https://github.com/jericho-lab/rdl

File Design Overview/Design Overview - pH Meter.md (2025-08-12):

**pH Meter Carrier Board Revision A1 - Design Overview**  
=======================================
Copyright: Jericho Laboratory Inc. License: CC-BY-SA.  

SAFETY WARNING: Always protect your skin and eyes when working with chemical products such as acids and bases.

WARNING: The following material is for educational purposes only. Always refer to the schematic and PCB layout files associated with your product version.

WARNING: Do not let the pH probe dry. When not in use, store the probe in KCL solution, not water. Do not let pH probe wire leads touch each other; a short circuit will damage the probe.

WARNING: Please read all documentation provided by Atlas Scientific about its EZO-pH, industrial probe before using the product. See references at the end of this document. This expensive equipment can be easily damaged if not used properly.

# Table of Contents

1. [GENERAL](#general)
2. [SOIL MEASUREMENTS](#soil-measurements)
3. [DESIGN GENESIS](#design-genesis)
4. [PROBE](#probe)
5. [PH METER CIRCUIT (EZO-pH by Atlas)](#ph-meter-circuit-ezo-ph-by-atlas)
6. [ANALOG ISOLATOR CIRCUIT](#analog-isolator-circuit)
7. [I2C COMMUNICATION](#i2c-communication)
8. [CALIBRATION OVERVIEW](#calibration-overview)
9. [OTHER](#other)
10. [REFERENCES](#references)

## GENERAL

- The pH meter system described in this document is modular: it is comprised of:
1) a Carrier board, designed by Jericho, 
2) a EZO-pH device, which must be inserted in the female header of the Carrier board.
Together, when connected to the RDL (Resistance Data Logger), they form a reliable pH meter.
- The EZO-pH has a polarity when inserted in the carrier. The drawing on the silkscreen helps the user remember the correct polarity. Powering on a system with an inverted polarity can damage the components. With the wrong polarity, the EZO-pH power LED will not light up.
- Note: The carrier board cannot make any measurement without the EZO-pH being inserted. The EZO-pH must be purchased from Jericho Lab or Scientific Atlas directly.
- The Carrier Board Design is entirely based on the public schematic shared by Atlas Scientific. The PDF schematic was recreated with the open-source software KiCAD, with some modifications and components substitution for improved functionality, availability and/or cost. A PCB layout was subsequently made for production with KiCAD as well.
- pH measurement are among the most common, yet the most difficult measurements. It has wide applications in chemical engineering, pharmaceuticals, laboratory experiments, environmental monitoring, swimming pools, aquariums, hydroponics, fish farming.
- The PCB components have not been tested at low temperature because the pH electrode cannot operate below freezing temperature. The water solution would freeze and expand and break.
- The design was made to be compatible with soil pH measurements and the RDL system.

## SOIL MEASUREMENTS

- Typical pH measurements target solutions, but this design was done with soil measurements in mind. Soil measurements are very useful in the context of agriculture. The user must make sure that the soil is excessively dry, which is why it should remain at a sufficient depth.
-  In the absence of aqueous solutions, the probe membrane will dehydrate and can be permanently damaged. In the event that the probe has dried up, a rehydration can be attempted by leaving the membrane in KCl solution (storage solution) at least 12 hours. 
- Soil mesurements can have variations and might provide inaccurate values in periods where the soil is becoming too dry for a sufficient contact with the membrane. ontrarely to river measuremets, where organic matters will rapidly accumulate through the passage of thousands of liters of water, the probe should not need frequent calibrations, being in relatively static environment.
- The intent of designing for soil measurements explains the choice of an industrial grade pH probe, which has two advantages:
  - an oversized solution reservoir (it will extend the life expectancy of a probe put in an environment that accelerates the consumption of the solution through the membrane)
  - a membrane with an improved resistance to harsh environments (e.g. sand, rocks)
- In the advent that the user is not planning to use the probe in soils, the user could select the other models - more affordable by Atlas, or any other traditional pH electrode. 

## DESIGN GENESIS

- There are very few reliable open-source designs to start from when designing a ph meter. 
  - The digital pH meter from Atlas could not be used as inspiration (US Patent 9571121B2, with equivalents in Canada, Japan, Great Britain, South Korea and WIPO). 
  - The analog pH meter from Atlas could not be used for the same reason (US Patent not found).
  - The DFRobot design could not be used because it appears to copy the one by Atlas Scientific - there is a trademark lawsuit between the US and Chinese companies. Although the trademark does not concern the schematic, it does raise concerns over intellectual property.

It was therefore decided to start with an open-source carrier board for the proprietary EZO-PH and keep the development of the core ph meter PCB for later.
- The goal of creating our own isolation board was to:
  - provide an integrated solution, with RJ45, 
  - provide a ready-to-modify, ready-to-build schematic and PCB layout, which Atlas did not provide.
  - Add a voltage regulator circuit for improved performance in situations where the 5V power supply cannot be guaranteed.
  - Remove the ability to turn off the EZO-pH, which was not useful in a multiplexed context.

## PROBE

- The pH meter revA1 must be used with a traditional pH electrode (combination silver-glass probe). Jericho has mostly experimented with and recommends the industrial probe, generation 3 by Atlas Scientific.
- The use of a shielded cable can be beneficial to the signal integrity of the probe. Cables are generally pre-assembled with the probe, and many will be shielded. In the case of the Atlas Industrial pH probe, the cable is NOT shielded.
- Electrical potentials produced by pH probe are very weak, and for example, one probe could have a range of -200 to +200mV. To limit the possible electrical interference, the cable length between the probe and the meter must be limited to a few meters. The cable provided by Atlas is 3m.
- The PCB connects to the probe via screw terminals (2 pins). If the selected pH probe has a connector (e.g. BNC, SMA), it can be cut or a standard adapter can be added.
- The pH probe wires have a polarity: black wire for ground (GND) and a copper wire for the probe signal (PRB). Make sure to respect this polarity when connecting the probe to the carrier board.
- When not in use, always protect either one of the probe wire leads with silicone tape. This will avoid any short circuit inside the probe, which would damage the probe.

## PH METER CIRCUIT (EZO-pH by Atlas)

- The pH meter subcircuit is the core of the device. It transforms raw electric potential from the probe into an analog signal, measurable by a data logger.
- Traditionally, the main components of a pH meter are an operational amplifier (op amp) and an instrumentation amplifier, but very little is known about the hardware and software of the EZO-pH device. The compiled code is kept in the EZO-pH processor and the user can interact with it via UART or I2C commands.
- Neither the pH meter hardware, nor software, include probe temperature compensation, since the error effect is very small (0.001 pH/°C) compared with the accuracy of the circuit (+/- 0.1 pH). Temperature does affects the pH of all solutions, but it is a real and separate phenomenon that must be captured by the probe.
- For its EZO-pH device, Atlas advertizes a +/- 0.002 pH accuracy, which appears unrealistic outside perfect laboratory environments. Jericho assumes the nominal accuracy of the pH meter in most environments to be no better than +/- 0.1 pH.

## ANALOG ISOLATOR CIRCUIT

- The main components of the Jericho analog isolator are:
  - an isolated power supply (B0505S).
  - a digital signal isolation circuit (ISO1540)
  - a voltage regulation circuit (TPS630701)

- The PCB has a measurement circuit and an isolator circuit. The signal isolator definition is an electrical device which is used to remove any earth loop (also called ground loop) errors which are caused by noise & signal interference problems. The isolator circuit ensures that the measurement is not biased by the nearby electrical fields, such as the one from a conductivity probe or a pump. The effect is more significant in a solution, but can also happen in soil.
- The analog isolator can use a 3.3V or 5.0V power supply. For standardization with the RDL platform, the 5V is selected. A voltage regulator circuit is added to improve the accuracy of the pH meter, since it is sensitive to the power supply fluctuations. It is the same circuit than the Jericho current sensor board. It operates in PFM mode with 1% accuracy on its 5V nominal value. For more information, read the NAU7802 design overview.

## I2C COMMUNICATION

- The EZO-pH can communicate via UART (i.e. Rx/Tx) or I2C protocols.
- By default, Atlas devices ships their EZO-PH in UART mode, which is simpler.
- Jericho ships their EZO-pH by default in I2C mode, to make it compatible with the RDL. EZO-PH is given a default I2C address of 99.
- There are two methods to change the active communication protocol: hardware or software.
  - The hardware methods requires connecting a jumper in between specific pins of the EZO-PH PCB.
  - The software methods consists in sending a UART command ("i2c,99) to switch to I2C, or a I2C command ("baud,9600") to switch to UART.
- Jericho uses the software method and provides two Arduino script to do so - one for each protocol. These are adaptation of public scripts by Atlas.

## CALIBRATION OVERVIEW
- To calibrate a probe-meter pair, the RDL must be loaded with a specific program, not the main RDL code. This specific program, called Ardunio-I2C-pH-sample-code-autorequest-v2.ino, is available in the calibration folder of the repo.
- This program assumes that the EZO-pH meter is already in I2C mode (it can operate in I2C or UART mode). To switch between the two modes, you can use two tiny programs located in: Source Code\Calibration-pH
- For detailed instructions about the pH meter calibration please refer to the Jericho calibration procedure available on Github.
- For pH measurements, the calibration is done with three buffer solutions that cover a large range of values. The three-point calibration is required because the response of the pH probe is not perfectly linear. The default pH values are 4, 7, 10 for pre-mixed liquid buffer solution. For powders, the pH values most often seen are 4.01, 6.86, 9.18. These powders are mixed with distilled water before use. Buffer powders have different pH values because they do not use the same chemicals. The limited range of the buffer solutions means that accuracy outside this range is unknown. The powders are generally more economic, more practical for transportation and more available. Their accuracy is judged sufficient (+/- 0.01 pH @ 25°C). Once mixed with water however, they have a limited shelf-life (hours to days). 
- The solution temperature must be known at calibration time. And the reference value must be adjusted in the code. For example, if the solution temperature is X Celcius, the nominal pH value of 4.01 is 4.05, and this value must be entered in the code as the reference value for the middle point. 
- The calibration procedure is convenient since the buffer solutions are relatively low risk, with pH values ranging from 4 (vinegar) to 10 (baking soda).
- The calibration results are registered inside the memory of the EZO-pH. There is no interaction with the RDL code. The calibration being specific to a given probe, each EZO-pH and probe form a pair that must not be undone. Otherwise, the calibration must be redone.

## OTHER

- There is no Power LED on the pH Carrier board, only the EZO-pH will indicate that it is powered on.

## REFERENCES

EZO-pH pH meter by Atlas Scientific,
https://atlas-scientific.com/embedded-solutions/ezo-ph-circuit/ 

EZO-pH pH meter by Atlas Scientific (Datasheet),
https://files.atlas-scientific.com/pH_EZO_Datasheet.pdf 

Industrial pH probe, gen 3, no temperature by Atlas Scientific
https://atlas-scientific.com/probes/industrial-gen3-ph-probe-nt/

Electrically Isolated EZO Carrier Board by Atlas Scientific
https://atlas-scientific.com/carrier-boards/electrically-isolated-ezo-carrier-board-gen-2/

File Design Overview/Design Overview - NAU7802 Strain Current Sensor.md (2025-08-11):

**NAU7802 Board For Strain and Current Revision B1 - Design Overview**  
=======================================
Copyright: Jericho Laboratory Inc.  
Document license: CC-BY-SA.  

**Warning**: The following material is for educational purposes only. Always refer to the schematic and PCB layout files associated with your product version, as well as the latest specification sheets of the associated electronic components.

**Safety warning**: You are responsible for your own safety. Always consult an accredited electrician before working with high-voltage electricity. This sensor operates with a low-voltage (5V) supply, but other components of your system might require an electrician. The L01Z sensor has no voltage protection against voltage spike or surge. However, the voltage regulator circuit adds some protection against voltage protection that might occur in the power supply.

**Warning**: This product is neither intended nor warranted for use in following equipment or devices: Special application (such as for medical devices, transportation equipment, traffic signal control equipment, fire and crime prevention equipment, aeronautics and space devices, nuclear power control, fuel control, in vehicle equipment safety devices, and so on) in which extremely high quality and high reliability is required, or if the malfunction or failures of product could be cause for loss of human life, bodily injury.

**Table of Contents** 

1. [INTRODUCTION](#introduction)
2. [ADC SUBCIRCUIT (NAU7802)](#adc-subcircuit-nau7802)
   - 2.1 [GENERALITIES](#generalities)
   - 2.2 [I2C COMMUNICATION](#i2c-communication)
   - 2.3 [MEASUREMENTS](#measurements)
3. [VOLTAGE REGULATOR SUBCIRCUIT (TPS630701)](#voltage-regulator-subcircuit-tps630701)
4. [STRAIN & FORCE MEASUREMENTS](#strain--force-measurements)
   - 4.1 [GENERALITIES AND INSTALLATION](#generalities-and-installation)
   - 4.2 [STRAIN GAUGE LOAD CELL (TAL220)](#strain-gauge-load-cell-tal220)
   - 4.3 [SOFTWARE](#software)
   - 4.4 [STRAIN SENSOR CALIBRATION](#strain-sensor-calibration)
       - 4.4.1 [INTERNAL CALIBRATION](#internal-calibration)
       - 4.4.2 [EXTERNAL CALIBRATION](#external-calibration)
   - 4.5 [RJ45 CONNECTORS](#rj45-connectors)
5. [ELECTRICAL CURRENT MEASUREMENTS](#electrical-current-measurements)
   - 5.1 [TAMURA L01Z050S05 SENSOR DESCRIPTION](#tamura-l01z050s05-sensor-description)
   - 5.2 [SENSOR OPERATION](#sensor-operation)
   - 5.3 [ANALOG OPERATION MODE](#analog-operation-mode)
   - 5.4 [DIGITAL OPERATION MODE](#digital-operation-mode)
   - 5.5 [ALGORITHMS (DC & RMS)](#algorithms-dc--rms)
       - 5.5.1 [DC AVERAGE](#dc-average)
       - 5.5.2 [SINE RMS](#sine-rms)
       - 5.5.3 [TRUE RMS](#true-rms)
6. [OTHER](#other)
7. [REFERENCES](#references)

## INTRODUCTION

- The NAU7802 board is a dual sensor PCB. A single design allows both electrical AC/DC current measurements (Hall Effect) and strain/force measurements with a gauge cell. This reduces the number of active designs at Jericho. 
-  Therefore, the same raw PCB is used for two separate Jericho products:
    - Jericho NAU7802 Strain Board;
    - Jericho NAU7802 Current Board;
- You will notice on the Strain Board that the TAMURA sensor absent, to reduce cost.
- It is in theory possible to use the Current board to make both times of measurements simultaneously (i.e. strain and current). However, this has not been tested yet and the magnetic field of the cable current is likely to induce noise and/or bias on the strain measurements.
- The current measurements can be done via the analog or digital mode, while the strain measurements can only be done via the digital mode.
- For general information about PCB designs of Jericho sensors, please refer to the 'Design Overview - General information' document.  
- The original design of this board was provided by Sparkfun (CC-BY-SA).
- The license for the Jericho improvements of the hardware is also CC-BY-SA.

## ADC SUBCIRCUIT (NAU7802)

- This section describes the details of the Analog-to-Digital (ADC) NAU7802 chip. The information is relevant to both current and strain measurements.

  ## GENERALITIES  
- The NAU7802 chip by Nuvoton is a high-accuracy voltage measurement device. It includes a 24-bit ADC (Analog-to-Digital Converter) and provides I2C communication.
- The NAU7802 has two main capabilities: it can provide a regulated voltage  and it has two channels to measure analog signals from sensors. The regulated voltage is typically used to excite a Wheatstone bridge (not used in this product).
- A very high accuracy ADC is required because the strain gauges, by their nature, create very weak signals, in the order of millivolts. The current sensor also needs the accuracy as it distributes a -50A/+50A input range on a 3V output range (+1.0V/+4.0V).
- The NAU7802 chip makes a differential voltage measurement by default. It can also be configured for single-end measurement (i.e. signal-to-ground).
- The VDDA and GND are respectively the excitation voltage and ground lines for the activation of the Wheatstone bridge. The A- and A+ pins are the actual measurements of the bridge.
- The NAU7802 chip is equipped with decoupling capacitors at the power supply (0.1uF, 10uF and 22uF). While other Jericho boards use only 0.1uF and 10uF, the NAU7802 uses a supplementary 22uF for increased stability.
- In theory, the NAU7802 does not require a precise supply voltage (2.7-5.5V) since it has an internal voltage regulator. However, multiple users of the similar Sparkfun NAU7802 board have reported on forums a high sensitivity of readings to voltage supply; hence, a voltage regulator circuit was added.
Similarly, the input decoupling capacitors, by stabilizing the input voltage, ease the work of the NAU7802 voltage regulator and improve performance by further reducing noise and other voltage fluctuations.
- Note that the NAU7802 can accept various voltage supply values but the reading voltage range will be limited by the supply voltage value (“AVDD should not exceed DVDD supply voltage”).
- When used with the RDL, the NAU7802 PCB is only supplied in power when a measurement is required by the RDL. This means that over the course of its life, the sensor will be powered up thousands of times. The NAU7802 chip does not require a delay between power up and reading; it deals with the necessary delays autonomously.

  ### I2C COMMUNICATION

- Like all sensors from the RDL suite, the NAU7802 board has been designed for long wire operation (30m). However, the NAU7802 chip appears to have a weaker native signal and achieves shorter cable lengths for a given I2C bus frequency. When combined with I2C shield, RDL, a CAT5 cable and low EM noise environment, the maximum cable length for continuous communication is currently 30 m.
- Apart from Sparkfun, there is another popular board design based on the NAU7802, by Adafruit. When comparing the two schematics, the stronger pullup resistors on the SDA/SCL lines (2.2kohm) seem to be the reason why longer cables are possible with Sparkfun than Adafruit (10kohm). On the Jericho design, as well as Sparkfun, these pullup resistors are in series with solder junctions (normally ON) that can be cut with a knife if the user wants to disconnect them.
- NAU7802 is designed to operate at 100kHz or 400kHz (high-speed I2C bus). However, it has shown no difficulties at operating at low bus frequency, down to 31kHz (Jericho present default on hardware-based I2C protocol).
- The presence of two RJ45 connectors on the board allows to daisy chain I2C devices. For example, the cabling cost can be reduced by using a single long cable to reach the strain sensor PCB and, from there, only add a short CAT cable to connect to the SHT40 PCB. This is possible because the two PCBs do not have the I2C address.
- The NAU7802 chip has a single permanent I2C address: 0x2A. Therefore, one cannot daisy-chain two strain boards, it can only daisy chain a different sensor. Using two strain sensors on a given system requires two separate channels.
- There is a supplementary 6-pin male header (2.54mm spacing) for quick connections and testing: GND, 5V, SDA, SCL, INT, VCC.

  ### MEASUREMENTS

- Although the strain and current measurements both use the same chip, NAU7802, they use it differently.
  - STRAIN: Differential mode
  - CURRENT: Unipolar mode

- The measurements can be done at various speed: 10, 20, 40, 80, 320 SPS (Samples Per Second). To reduce sampling time, the RDL runs at 320 SPS by default.
- The DVDD pin is the digital power supply input (2.7 - 5.5V). It is externally provided by the on-board regulating circuit (5V).
- The VDDA pin is the analog power supply input (2.7 - 5.5V), used to excite the Wheatstone bridge. The default manufacturer value is 3.3V, supplied by NAU7802 internal circuit. In the present case, this default mode is overriden (via NAU7802 registers) and instead the DVDD signal is used (5V). It is within the allowable excitation voltage range of the TAL220 (3-10V) and it maximize the measurement range by maximizing the sensitivity (V/N). Accordingly, the ADC voltage range is also modified within the code. For more information, read the RDL source code and the RDL code documentation.
- The PGA (Programmable Gain Amplifier) can be configured to vary the gain applicable (1, 2, 4, 8, 16, 32, 64, 128). It also affects the voltage range applicable. The default value is 128. This gain could be reduced if the load cell output measurement was saturated by the NAU7802 chip. The PGA must be deactivated for unipolar mode (current measurements).
- The measurement output by the NAU7802 is the average of a large sample. This is configured within the Arduino code. 
- The ADC output follows this general equation: “ADC Output Value = Gain_Calibration\* (ADC measurement - Offset_Calibration)”.

## VOLTAGE REGULATOR SUBCIRCUIT (TPS630701)

- This section describes the details of the voltage regulation subcircuit. The information is relevant to both current and strain measurements.

- To supply a high accuracy 5V line to the current sensor, the TPS630701 chip (buck-boost converter with switch current) is used.
- The circuitry around the TPS630701 is based on the manufacturer recommendation presented in the specification sheet.
- Four (4) decoupling capacitors are added on the input and output of the TPS630701 to improve the performance and stability.
- This chip has two operation modes: PWM (Pulse Width Modulation) and PFM mode (Pulse Frequency Modulation) . The first is more efficient, the second is more accurate. The PWM mode has a +1/-3% accuracy, which is insufficient for the need of the TAMURA sensor. The PFM mode achieves a +/-1% accuracy, which is the minimum requirement for the TAMURA sensor. To activate the PFM mode, the pin ‘PS/SYNC’ is pulled high.
- A male header is added to give access to some of the TPS63070 pins, but in normal operations they are not required. These pins are: VOUT, PG, GND, PS, GND, EN, VIN.
- A heat sink of dimension 0.19x0.25x0.30" is optional but generally recommended for the TPS630701 chip. No heat sink is added for the NAU7802 board since the power consumption is so low (15mA) compared with the nominal capacity (2A).
- TPS630701 is the fixed output version (5V) of the TPS63070 (adjustable output 2.5 - 9V). Contrarily to the Sparkfun original design, this circuit uses the fixed 5V output version. It has no feedback resistor to adjust the output between 2.5 and 9V. Instead, it has a feedback resistor inside the chip. The feedback resistor has an effect on the accuracy of the output, and so the accuracy (unknown) of the inner resistor is possibly what limits the accuracy achievable according to specsheet (i.e. +/- 1%). Using the fixed 5V output has the advantage of avoiding any confusion that could occur with the variable voltage version.
- A LED is added to the subcircuit to indicate that the sensor is powered on. If the voltage regulator circuit is out of service, the LED will not turn on. However, the LED turning on does not confirm that the regulation is within specs, as the LED can turn on at lower voltages than 5V.
- You will notice a high-frequency noise while the ADS1115 operates. You will also notice a ticking sound at power startup, due to the coil being energized. These two sounds are considered normal with this design.
- The L01Z sensor has no voltage protection against voltage spike or surge. However, the voltage regulator circuit adds some protection against voltage protection that might occur in the power supply. On the measurement side, a sudden spike in current can produce an unexpectedly strong magnetic field, which could lead to erroneous readings or potentially damage the sensor if it exceeds the sensor's maximum current rating.

 ## STRAIN & FORCE MEASUREMENTS

 - This section describes the subcircuit responsible for strain and force measurements.

   ## GENERALITIES AND INSTALLATION  

- To operate, a strain sensor board requires a separate strain gauge load cell. This section details the relationship of the sensor with the required load cell.
- The J3 screw terminal allows the PCB to connect with the strain gauge load cell. The load cell should be a full Wheatstone bridge. The wire colors on a load cell tend to indicate the function but it might differ on your specific load cell. In case of conflict, the wire function (VDDA, GND, A-, A+) has priority over wire color.
- A Wheatstone bridge is an electrical circuit used to precisely measure an unknown electrical resistance by balancing two legs of a bridge circuit, one leg of which includes the unknown component. It is commonly used in sensor applications to convert changes in physical phenomena (like temperature, strain, or pressure) into changes in resistance, which can then be measured with high accuracy.
- As a general rule of thumb, the wire length between the NAU7802 and the strain gauge must be minimized and be kept under 1 m. This helps keep the signal-to-noise ratio at a sufficient level.
- The detailed installation procedure for strain gauges goes beyond the scope of this document but is a crucial part of the process.
- Since strain gauge load cell wires are usually quite small and small gauge wires can slip out of the 5mm terminal, this PCB design uses smaller screw terminals: 3.5mm pitch instead of the typical 5mm pitch. 
- By their nature, strain gauges do not tolerate well long-term static loads (> 1 day). It causes measurement drift for multiple reasons (gauge deformation, adhesive breakdown). For precise long-term measurements, periodic recalibration and the use of multiple gauges for redundancy may also be necessary.

  ## STRAIN GAUGE LOAD CELL (TAL220)  

  - For general use, we recommend the following load cell: TAL220 (micro parallel beam) by HTC-sensor (Chinese manufacturer). For more information, consult the TAL220 specification sheet. You can buy the TAL220 on Sparkfun.com or on the manufacturer website (htc-sensor.com). The manufacturer has more production options (e.g. load capacity from 1kg to 50kg, outdoor jacket, etc). The TAL220 has IP65 rating.

  ## SOFTWARE

- The standard RDL code can operate the strain sensor. The number of allowable strain sensors is only limited by the number of I2C channels.

  ## STRAIN SENSOR CALIBRATION

- When measuring strain with a NAU7802, there are two types of calibration: internal, external. The internal calibration makes sure that the strain gauge is accurately measured by the NAU7802 ADC. The external calibration ensures that the strain gauge resistance is accurately converted into a force or strain.

  ## INTERNAL CALIBRATION
- According to the NAU7802 manufacturer, the internal calibration is recommended after each of the following events:
  1) initial power-up
  2) power-up after long-duration register mediated power-down conditions
  3) PGA gain value change
  4) power supply change
  5) significant temperature changes (can be measured using built-in thermal sensing feature)
  6) sample rate change 
  7) channel select change. 

  This list excludes the frequent powerups that occur due to a potential multiplexer (i.e. RDL).
- For the RDL, internal calibration is done automatically by a function from the NAU7802 library (calibrateAFE()). It is called at powerup and at a regular interval. The algorithm is still under development for the regular interval.

  ## EXTERNAL CALIBRATION
   
   Each load cell requires its own unique calibration coefficients. Because of this, once calibration is performed, do not interchange strain gauges between channels. For example, strain gauge #1 must always remain in I²C channel #1.
   
   ### Why Individual Calibration Is Necessary
   •	Every load cell has slightly different electrical properties.
   •	Calibration produces two unique parameters per load cell:
   o	a = slope (gain)
   o	b = offset (zero point)
   •	This two-parameter calibration is sufficient because load cells are highly linear devices.
   We recommend attaching a weatherproof identification tag to each load cell to avoid mix-ups.
   If the load cell is damaged or replaced, a calibration must be done. 
   
   ### Calibration Process
   Calibration is performed manually:
   1.	Use a significant calibration weight to determine the slope coefficient (a). We recommend a default of limited weight of 1 kg to simplify manipulations and reduce the risk of injury.
   2.	Ensure the calibration weight does not exceed the load cell’s rated capacity. The TAL220 model is available in capacities from 3 to 50 kg.
   
   ### Coefficient File Workflow
   The source code repository includes a folder named “Coeff_gen”, containing all necessary files for creating a calibration coefficient file compatible with the main Arduino code.
   1.	coefficients_source.xls – Input file
   o	Fill this Excel file manually following the embedded instructions.
   o	This file holds the raw calibration values (a, b) for each load cell.
   2.	runMe.py – Processing script
   o	This Python script reads coefficients_source.xls and generates the output file coefficients.h.
   3.	coefficients.h – Output file
   o	Contains an 8 × 2 float matrix with the coefficients (a, b) for up to 8 I²C channels (maximum 8 strain sensors).
   o	The matrix size must remain constant. Empty channels must contain zeros.
   o	No default values are provided because:
   1.	Calibration values—especially b—vary significantly between units.
   2.	Default values might mislead users into thinking calibration has already been completed.
   
   Calibration values can only be updated by compiling again the source code; it currently cannot be done via a Serial Monitor command.

  ## RJ45 CONNECTORS

- There are two RJ45 connectors on this board, which allow I2C communication. They are not compatible with the Ethernet protocol. They are interchangeable. One can be used for connection to the RDL, the other for daisy-chaining.
- Each connector follows the following wiring connection:
  - Pin 1 & 2: VCC
  - Pin 3 & 4: GND
  - Pin 5 & 6: SDA
  - Pin 7 & 8: SCL
- This wiring order, combined with the internal architecture of the CAT cable (standard) creates a partial shielding, since the GND wires are twisted with the VCC and SDA wires. In future versions, improvements could be made on the wiring order to also shield the SCL line.
- For the strain sub-circuit, the main modifications with the Sparkfun design are: 1) the addition of a voltage regulator circuit; 2) the addition of RJ45 connectors; and 3) the addition of screw terminals.
- The NAU7802 chip itself has some sensitivity to temperature. There are two ways to protect the measurements from temperature bias: 1) internal calibration at a regular interval; 2) on-chip temperature measurement. Due to the complexity of the second method (which is not coded in the Sparkfun library), only the first method is used. The temperature data is not exposed to the I2C interface. 

- Strain gauges are very sensitive to temperature variation. There are multiple components to this relationship (e.g. load cell thermal expansion, strain gauge film expansion). However, some Wheatstone configurations are inherently compensated in temperature. This is the case for the TAL220 (parallel bending cell with full bridge). Therefore, the thermal expansion will affect both strain gauges in the same way and cancel each other out in the voltage output. This technique is effective within a mild temperature range (e.g. -10 to +40C). At extreme temperature, independent external temperature compensation via a separate thermistor probe can be required (not coded).

## ELECTRICAL CURRENT MEASUREMENTS

- This section describes the current measurement section of the PCB.  

  ## SENSOR DESCRIPTION (TAMURA L01Z050S05)

- The core component of the board is the L01Z050S05 current sensor module manufactured by TAMURA Corporation (a global company with head offices in Japan). The L01Z module, based on the Hall effect, can measure both DC and AC (up to 100kHz) current up to 50A DC. The maximum frequency readable by the Jericho board however is much less, limited by the sampling speed of the processors. The LZ01 series offers module with a capacity up to 600A DC.
- The L01Z component was selected because it can be used with AC and DC current, while as induction-based sensors are only compatible with AC current.
- The TAMURA component is readily available at global suppliers like DigiKey or Mouser. PCB manufacturers like JLCPCB can source from those suppliers for their SMD and through-hole assembly line.
- The TAMURA module was designed for indoor use and is not weatherproof. Therefore, the sensor MUST be installed in a weatherproof enclosure to avoid any damage or safety risk.

  ## PCB INTEGRATION

 - The TAMURA is a through-hole component soldered on the PCB. Two soldered mechanical pins reduce the strain on the electronic pins.
 - The analog output is a 0-5V output, but for several reasons, it requires a load resistor (RL):
    - Voltage Division (scale down the voltage to ADC level)  
    - Current limiting
    - Signal conditioning (provide a predicatble load impedance)
    - Interface Matching (Match the input impedance to avoid signal loss)
 - The manufacturer specifications require a 10 kohms load resistor. More information is available in the L01Z Series Application Manual.

  <figure>
  <p align="center">
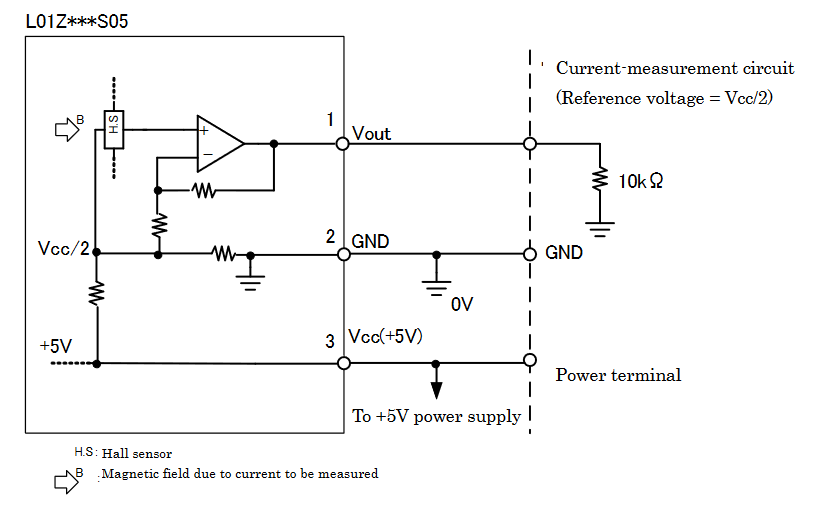
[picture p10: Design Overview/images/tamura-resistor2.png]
   
 </figure>
 <p align="center"> Recommended electrical circuit for the L01Z sensor (Copyright TAMURA CORP)

  ## SENSOR OPERATION

- To make a measurement, a single conductor must pass through the core. If both the supply and return conductors pass through, the sensor will measure a value near zero, since the two electrical fields will cancel each other.
- The TAMURA design is NOT a clamp design. The cable has to be securely disconnected from the source and passed through the core.
- The maximum size of wire gauge that can fit into the TAMURA core is limited. The cable – with its insulation – must fit into an 8mm x 15mm rectangular opening.
- The module can work from -20 to 80°C. Therefore, in most cold climates, there is no need to add a heating module. The rest of the components such as the voltage regulator can also tolerate those temperatures. In the near future, the module accuracy will be tested at -40°C. It is expected that the sensor will function properly but potentially with a reduced accuracy.
- According to L01Z specifications, the sensor accuracy at nominal current (i.e., 50A DC) and nominal temperature is ±1%. However, this is dependent on a high accuracy voltage supply: 5V ± 2%. For this reason, a voltage regulator was added to the board.
- The L01Z module has 3 pins: voltage (VCC), ground (GND), signal (SIG). The signal data is an analog 0-5V signal. This signal can be read by the analog channels of the RDL RevE2. The sensor can read positive and negative DC currents. Positive currents go from the reference voltage (V_ref) to 5V. Negative currents go from the reference voltage to 0V.
- The TAMURA consumes up to 15mA, which can cause a voltage drop on longer power supply cables (Ohm's law). This is the second reason - beside accuracy - why the voltage regulator subcircuit is essential. For the signal cable, the current is much reduced, reducing significantly the voltage drop. The RDL can therefore measure the signal directly with its ADS1115 chip, if desired.
- Due to its two RJ45 connectors, the NAU7802 board is compatible with daisy-chain, if there is no I2C addresses conflict.

  ## ANALOG OPERATION MODE

- The analog mode consist of taking direct measurements of the TAMURA sensor output (0-5V) with the RDL ADS1115 chip.
- This mode is less precise due to: 
    1) reduced ADC resolution (NAU7802 has 24-bit, while the ADS1115 has 16-bit resolution)
    2) analog signal is sensitive to E.M. noise and voltage loss  
- The analog mode is only accessible via the screw terminal (VCC, GND, DATA). It is not available via the RJ45 connectors.
- The analog mode is therefore not recommended if the digital mode is available.

  ## DIGITAL OPERATION MODE

- The digital mode builds upon the analog mode. A high-accuracy ADC chip, NAU7802, measures the analog signal and converts it to a digital I2C signal that is transmitted to the data logger.
- The NAU7802 defaults to differential measurements (A+, A-) but for the current measurements, it operates in unipolar mode (A+, GND). The PGA is also deactivated to increase the measurement range to a full 0-5V.
- The Jericho NAU7802 board has dual purpose: current measurement and strain measurements. This is made possible by the dual-channel NAU7802. Channel A (A+, A-) is dedicated to current measurement, while Channel B (B+, B-) is dedicated to strain measurements (i.e. Wheatstone bridge). 

  ## EFFECTIVE CURRENT ALGORITHMS

- The RDL has three algorithms for the measurement of current. The algorithm affects both the sampling method and the data treatment. It does not affect the current sensor itself. 

    ### DC AVERAGE

  - A simple arithmetic average of a variable-size sample. Useful for DC currents only.

  ### SINE RMS (NOT IMPLEMENTED YET)

  - Sine RMS (Root Mean Square) is used for AC measurements where the waveform is predominantly sinusoidal. This method provides an efficient computation by leveraging the properties of a sine wave. It rectifies the signal and applies a correction factor.

  ### TRUE RMS  (NOT IMPLEMENTED YET)

  -  True RMS calculation provides accurate readings for AC currents regardless of waveform shape, making it essential for electronic applications involving non-linear loads.
  - The True RMS algorithm, and to a lesser extent the Sine RMS, require high-speed data processing. The limited Arduino Nano speed therefore poses a limit to the maximum allowable frequency of AC signal that can be measured.

  ## SOFTWARE

- The standard RDL code can operate the current sensor in both the digital mode (I2C) and analog mode.
- In digital mode, the number of current sensors is limited by the number of available I2C channels (max 8). In analog mode, it is limited by the number of available analog channels (max 8).

## OTHER

- The board has 3.5mm diameter holes in each corner for installation purposes.
- Jericho recommends the use of two adequate size cable glands (inlet, outlet) on the main cable to avoid any water entry in the enclosure.
- Jericho recommends the addition of silica gel packet inside the enclosure to reduce humidity.

## REFERENCES

NAU7802 specsheet

https://www.nuvoton.com/resource-files/NAU7802%20Data%20Sheet%20V1.7.pdf

TAMURA LZ01 Series Specsheet

https://www.tamuracorp.com/clientuploads/pdfs/engineeringdocs/L01ZXXXS05.pdf

L01Z Series Application Manual

https://www.tamuracorp.com/file.jsp?id=18591

HTC-Sensor TAL220 Specsheet

https://www.digikey.com/htmldatasheets/production/2459755/0/0/1/tal220.html

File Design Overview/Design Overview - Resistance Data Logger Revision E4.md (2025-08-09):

**Resistance Data Logger (RDL) Revision E4 - Design Overview**  
=======================================
Copyright: Jericho Laboratory Inc.  
Document License: CC-BY-SA.  

**Warning**: The following material is for educational purposes only. Always refer to the schematic and PCB layout files associated with your product version.

**Safety warning**: You are responsible for your own safety. Always consult an accredited electrician before working with high-voltage electricity. This sensor operates with a low-voltage (5-12V) supply, but other components of your system might require an electrician. Do NOT install in areas prone to thunder as the system has no protection against thunder. It is recommended to NOT open the main enclosure during bad weather (rain, snow, dust) to minimize the risk of component damage and safety issues.

**Warning**: This product is neither intended nor warranted for use in following equipment or devices: Special application (such as for medical devices, transportation equipment, traffic signal control equipment, fire and crime prevention equipment, aeronautics and space devices, nuclear power control, fuel control, in vehicle equipment safety devices, and so on) in which extremely high quality and high reliability is required, or if the malfunction or failures of product could be cause for loss of human life, bodily injury.

# Table of Contents

1. [GENERAL](#general)
2. [NANO](#nano)
3. [REAL TIME CLOCK (RTC)](#real-time-clock-rtc)
4. [THERMISTOR/RESISTIVE CHANNELS](#thermistorresistive-channels)
5. [I2C COMMUNICATION](#i2c-communication)
6. [ANALOG MEASUREMENT SUBCIRCUIT](#analog-measurement-subcircuit)
7. [CONTROL SIGNAL](#control-signal)
8. [OTHER](#other)

## GENERAL

- This document refers to the Resistance Data Logger (RDL) system associated with the Jericho RDL PCB revision E4. 
- The RDL hardware is released under the MIT open-source license.
- The current board revision only works with the corresponding source code revision.
- Allowable wire gauges are written on the silkscreen (AWG 20-26). This is the ideal size to avoid wires slipping out. The order of the terminals is also printed (i.e. VCC, GND, SIG, VCC, GND, SIG, etc.)
- Starting with revision E2, the objective of maintaining at least 50% of the product cost (material and labor) has been abandoned. This was a requirement for the ‘Made in Canada’ label, which appeared contrary to the goal of maximizing affordability and access. Therefore, outsourcing is maximized, including SMD and through-hole components.
- Long wires (>10m) between the RDL and its sensors will cause significant voltage loss. This means that some devices will require a voltage regulator at the other end to make sure that the chip is supplied with the proper voltage.
- There are holes around the board to help attach the wires and reduce mechanical stress on the wires.

## NANO

- The Nano refers to the Arduino Nano clones that are sold throughout the world by third party manufacturers. ELEGOO is one such manufacturer, which has the benefits of containing the new bootloader (see Arduino IDE). The "old bootloader" tends to provoke errors when uploading the RDL code.
- The Nano clone is inserted in the dedicated female headers and is removable by hand for purposes of replacement or maintenance. This modularity reduces cost and increases product resilience. It allows the user to bring the Nano indoors to upload a new code. It also opens the door to major upgrades, such as the Arduino Nano ESP32, which can run Python and AI Edge but has the same pinout than the Nano. Only the 3.3V supply would be challenging.
- Of course, since the Nano ELEGOO is removable, it can be substituted with any other Nano manufacturer.
- A second row of female header is present to allow temporary connections to all pins via hookup wires. 
- Decoupling capacitors are added to all devices to reduce voltage variations on the power supply. This includes the Nano and the following chips: DS3231, CD74HC4051, PCF8574T, LTC4311, ADS1115. All decoupling capacitors are done with a 0.1uF and 10uF caps. Note that the Nano has internal decoupling capacitors, creating a redundancy.
- It is worth noting that the Nano does not operate at a regulated voltage if connected to a USB port. The USB port itself has some degree of voltage regulation but as the current consumed by the RDL varies, the voltage loss (Ohm law) on the USB cable will vary, resulting in a voltage that varies typically between 4.2 and 4.95V.

## REAL TIME CLOCK (RTC)

- The RTC chip is the DS3231MZ+. The internal oscillator of the clock chip is temperature compensated internally. Operation in cold temperatures should have minimal impact on long-term timestamp accuracy.
- The chip has backup power via the 3V CR1220 battery holder. At extremely low temperature, the voltage of an ordinary CR1220 battery is reduced and can become insufficient for the RTC operation (not tested). The phenomenon is reduced by locating the RDL inside the main enclosure, which benefits from the Pi waste heat.
- The DS3231 communicates via I2C protocol to the Nano. In theory, it only communicates at the standard bus rate of 100Khz. However, tests have shown that it performs well even at 31. Being able to operate all I2C devices on the same bus speed simplifies the product (there is a single I2C bus on the system).
- The positive side of the CR1220 battery is only connected to the RTC clock, and so the I2C bus will not be activated and drawing power from the battery (the RTC chip is a slave I2C device).

## THERMISTOR/RESISTIVE CHANNELS

- The resistive channels are multiplexed on both the high and low sides of the voltage divider. The multiplexing is done via two multiplexers of the CD74HC4051 series. This avoids having a lot of EM noise on the power supply lines (power and ground) that would occur when using 30m lead wires. The CD74 multiplexers are controlled simultaneously via 3 analog pins. This is possible on the RDL and not on the I2C shield because we have easy access to the Nano Shield is only connected to the RDL via the CAT cable (VCC, GND, SDA, SCL).
- The on-resistance of the multiplexers (2) is taken into account in the source code, despite its low value (2 x 70 ohms).
- The two multiplexers are synchronized. They are controlled with the same Nano digital pin. Their channels are controlled with the same digital pins (D2, D3, D4). This simplifies the board wiring, as well as the software. It also leaves more analog pins for other usage.
- The resistor for the voltage divider circuit is a high-accuracy (+/- 0.1%) surface-mounted device (SMD).
- The voltage divider can be measured by two methods. 
  1) The signal can be measured by the Nano analog pin A0. This method has a limited accuracy due to the 10-bit ADC of the Nano and now serves as a backup. 
  2) Second, the voltage divider signal can be measured by the ADS1115 chip. This 16-bit chip has four single-channels. For more information, read the ADS1115 section.
- Neither method (A0, ADS) uses a pulldown resistor. Although this would help display a clean, stable value ("0.0000") when the channel is empty, even a weak pulldown would bias the readings significantly when the thermistor takes a high resistance (near 1 MΩ) value at low temperature.

## I2C COMMUNICATION

- Apart from the resistive and analog sensors, the main method to integrate and communicate with sensors is via the I2C protocol.
- By default, the Nano operates at standard I2C bus clock speed of 100,000 Hz. This speed however is incompatible with very long cables (>10m) due to the high capacitance of cables, which deform the I2C square wave beyond recognition. It is therefore best to reduce the frequency.
- By default, the RDL code operates the I2C bus line at 490Hz. This is achieved by modifying the core parameters of the Wire library before compiling the Arduino code. More precisely, the TWBR and prescalers values of the twi.c file are modified. A ready-to-use modified Wire library is available in the Jericho source code.
- There are two ways to communicate via I2C protocol on this board: the RJ45 connector and the I2C screw terminals. The RJ45 is useful for permanent uses and long wire connections, while the screw terminal is useful for quick tests. The screw terminal can also serve as a temporary location for pull-up resistors on the SDA and/or SCL line.
- The LTC4311 chip is an I2C booster. Together with the pullup resistors and the slow I2C bus clock, it allows communications over long cables. The LTC4311 is located on the RDL board instead of the I2C shield for two reasons: 1) allow long wires even without the use of an I2C shield; 2) avoid having multiple LTC chip on the same I2C bus (conflict) when more than one I2C shield is added.
- The board has holes for the standoffs that allows the I2C shield to be installed beneath the RDL. The installation is best done with the shield beneath the RDL in order to leave an easy access to the Nano pins and buttons. Installation cannot be done above the RDL unless longer standoffs are used than those provide if the the Nano ICSP pins are to be cleared.
- Up to three I2C shields can be stacked, providing 25 I2C connections (3 x 8 + 1 on the RDL). Three is the theoretical limit since the TCA9548 chips have eight I2C addresses possible, and a three-shield stack will use seven of those. The daisy chaining of sensors can be applied to increase that number. For more information, refer to the I2C shield Design Overview document.
- Any subtype of CAT cable will work: CAT5, CAT5e, CAT6, CAT7. Other than the variation on cost, size and weight, these cables have different ability to protect the signal from EM noise. They might also have different capacitance per unit length, which affect the maximum usable cable length.
- The 8-pins wiring of the RJ45 does not follow a standard. The wiring order is:
  - Pin 1 & 2: VCC
  - Pin 3 & 4: GND
  - Pin 5 & 6: SDA
  - Pin 7 & 8: SCL
- This pin order, combined with the internal standard architecture of the CAT cable (either EIA568A or EIA568B) creates a partial EM shielding, since the GND wires are twisted with the VCC and SDA wires. In future versions, improvements will be tested on the wiring order.

## ANALOG MEASUREMENT SUBCIRCUIT

- The RDL has eight (8) multiplexed channels for analog signal (0-5V) measurements. Each channel is made of three (3) pins: Power (VCC), Ground (GND) and Signal (SIG). The power and ground pins are multiplexed via a PCF8574 chip and MOSFETS. The signal pins are multiplexed via a CD74HC4051 chip.
- Using the same logic than the resistive measurement, the analog measurements can also be done via two methods: the analog pin A1 on the Nano (10-bit ADC), and the channel 1 pin on ADS1115 (16-bit ADC).
- The ADS1115 two remaining channels (i.e. 3 & 4) are connected to the 5V and 3.3V pins of the Nano. It is useful to measure the 3.3V pin, only in the case of measuring the voltage divider with the ADS1115. This is because the ADS1115 is not referenced to the same voltage than the Nano. Therefore, the supply voltage of the voltage divider does not cancel itself in the equation as it does when the measurement is done by the Nano ADC, referenced to the same 3.3V. Therefore, the 3.3V must be measured accurately. The 5V measurement is useful to determine the conditions under which the ADS1115 operates, since it cannot measure voltages higher than its own supply voltage.
- According to manufacturer speciications, the ADS1115 has a minimum I2C clock speed requirement of 10 kHz. In theory, this recommendation puts a limit to slowing the clock, although it could be tested lower.
- The same concept of double multiplexing is applied to analog voltage measurements. However, the operation is different for the VCC and GND lines due to the use of transistors. We are forced to use transistors because the CD74 chip is very limited in the current it can transmit (~10-50mA). The Nano can supply as much as 500 mA (USB limit). To be able to supply this amount, MOSFET transistors are used (p-channel (AO3401A) and n-channel (AO3406)). Since the subcircuit is substantially the same than the one for the I2C shield, refer to the I2C shield Design Overview for more information.
- The decoupling capacitors circuit of the ADS1115 is different than those of other chips: it also includes ferrite beads that help reduce the increased noise caused by the ADS1115. This prevents contamination of the entire power buses. A ferrite bead act as an inductor who let pass low-frequency but blocks high frequency signals (i.e. noise).
- The PCF8574 chip is an GPIO (General Purpose Input/Output) expander. It can be thought of as an open drain configuration and has a modifiable I2C address. Since you cannot have two devices with the same I2C address on a given I2C bus, each of the two PCF on the RDL has a different address. This is done via solder jumpers. The PCB layout uses two different addresses to avoid any soldering from the user. There are also 10k resistor to limit the in-rush current to the address pins.

## CONTROL SIGNAL

- For non-critical operations (see the User Guide and General Design disclaimers), the RDL can provide a 0-5V control signal.
- This control signal is most easily produced by the screw terminals via the "D9" identified channel. This channel is connected to pin D9 of the Nano. This pin is ideal due to its ability to have Pulse-Width Modulation (PWM) signals. Only certain pins on the Nano can provide such PWM signals: D3, D5, D6, D9, D10, D11.
- Note that PWM signals perform poorly on long wires, whose high capacitance blurs the PWM exact signal shape. The D9 pin can also provide a binary output (low/high) but it cannot provide a true analog output, since the Nano has no DAC (Digital-to-Analog Converter). For more information on the various types of signal output, refer to the official Arduino Nano documentation.

## OTHER

- The RDL board has no power LED. Only the Nano LED indicates proper power and operation.
- The channels 1 and 8 of the analog voltage measurements both have a power LED to help the user diagnose the proper operation of their code. If the LED of channel 1 does not power on, the sensor connected to channel 1 has no power. The lighting of the LED however does not confirm that the RDL is properly reading the sensor signal though.

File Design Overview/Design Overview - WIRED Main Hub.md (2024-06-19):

**WIRED Main Hub Revision A1 - Design Overview**  
=======================================
Copyright: Jericho Laboratory Inc.  
Document License: CC-BY-SA.  

**Warning**: The following material is for educational purposes only. Always refer to the specific documents (e.g. schematic) associated with your product version.

**Safety warning**: You are responsible for your own safety. Always consult an accredited electrician before working with high-voltage electricity. This sensor operates with a low-voltage (5-12V) supply, but other components of your system might require an electrician. Do NOT install in areas prone to thunder as the system has no protection against thunder. It is recommended to NOT open the main enclosure during bad weather (rain, snow, dust) to minimize the risk of component damage and safety issues.

**Warning**: This product is neither intended nor warranted for use in following equipment or devices: Special application (such as for medical devices, transportation equipment, traffic signal control equipment, fire and crime prevention equipment, aeronautics and space devices, nuclear power control, fuel control, in vehicle equipment safety devices, and so on) in which extremely high quality and high reliability is required, or if the malfunction or failures of product could be cause for loss of human life, bodily injury.

******** THE DOCUMENT IS AMBIGUOUS BETWEEN ORANGE PI AND RASPBERRY PI ********
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

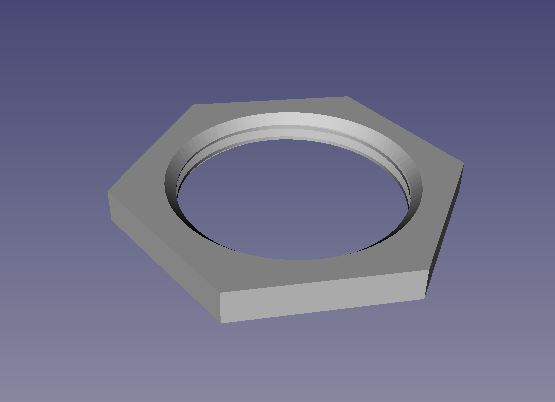
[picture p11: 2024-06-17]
Design Overview/images/camera_nut_v6.JPG

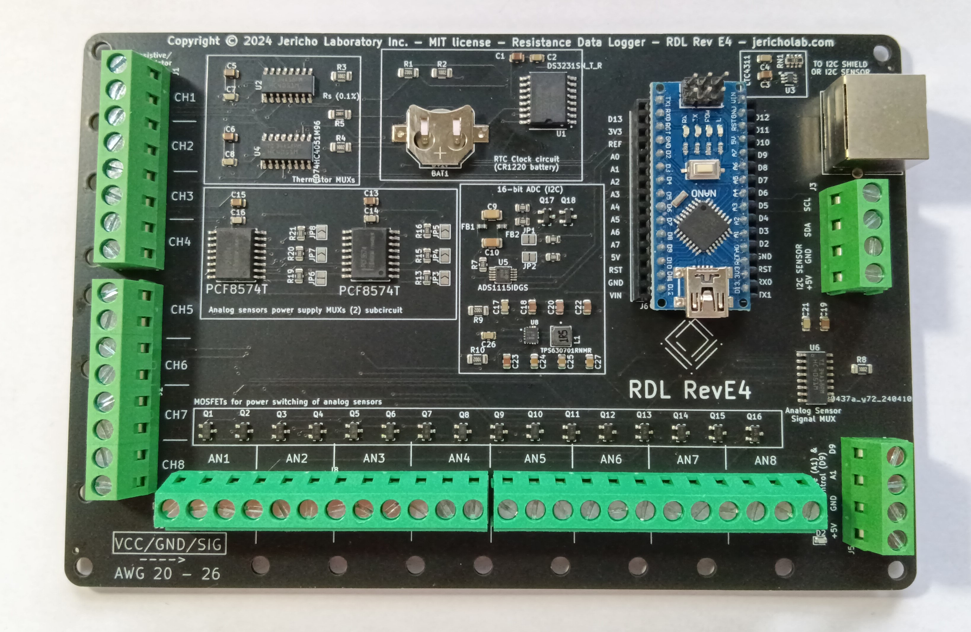
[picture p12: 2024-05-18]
PCB Design/images/Picture-RDL-revE4-croppedCopy.jpg

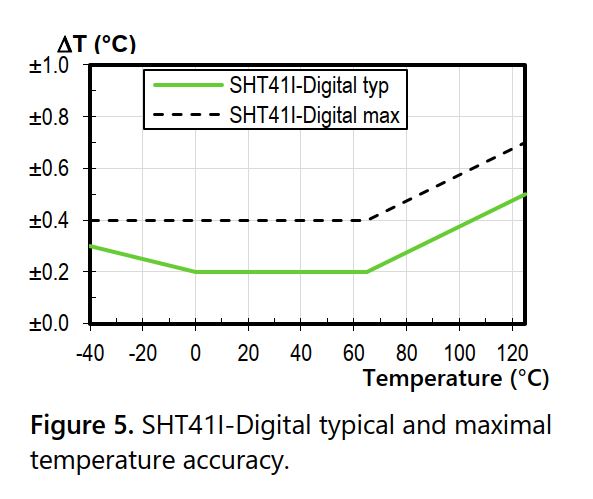
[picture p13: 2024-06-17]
Design Overview/images/img2-sensirion-sht41I-temp.JPG

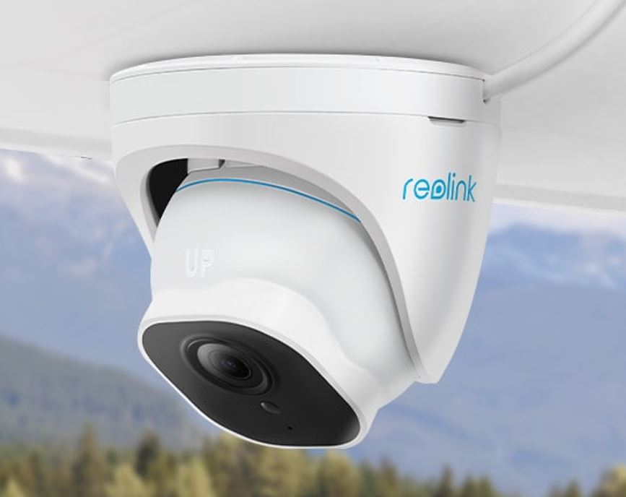
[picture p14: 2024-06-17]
Design Overview/images/Reolink-rlc-520a.jpg

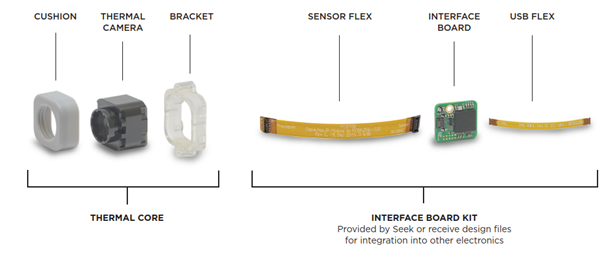
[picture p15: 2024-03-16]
Design Overview/images/1 IR Camera RevA1.png

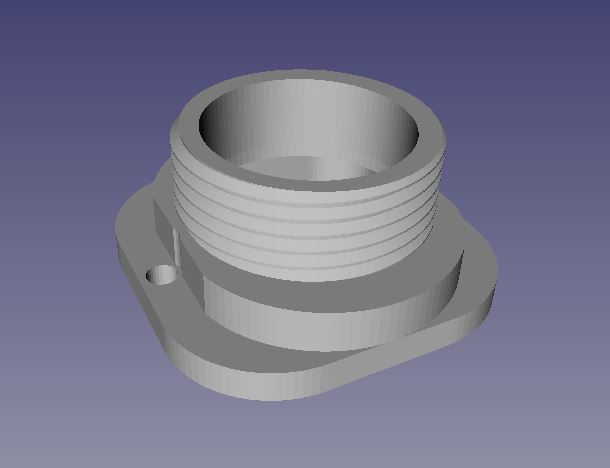
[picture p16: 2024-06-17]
Design Overview/images/camera_holder_v10.JPG

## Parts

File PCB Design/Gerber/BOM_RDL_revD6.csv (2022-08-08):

Comment | Designator | Footprint | LCSC Part Number
10k | R1 | Resistor_SMD:R_1206_3216Metric | C17902
10k | R2 | Resistor_SMD:R_1206_3216Metric | C17902
1k | R3 | Resistor_SMD:R_1206_3216Metric | C4410
1 uF | C1 | Capacitor_SMD:C_1206_3216Metric | C1848
3V | BAT1 | Battery:BatteryHolder_Keystone_3000_1x12mm | C964818
DS1307ZN+ | U1 | SOIC-8_3.9x4.9mm_P1.27mm | C26858
CD74HC4067M96 | U2 | digikey-footprints:SOIC-24_W7.50mm | C496123
Crystal | Y1 | Crystal_SMD_Abracon_ABS25-4Pin_8.0x3.8mm | C454602

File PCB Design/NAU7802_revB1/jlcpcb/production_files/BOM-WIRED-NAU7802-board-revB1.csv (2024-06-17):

Comment | Designator | Footprint | LCSC
10uF | C11,C5,C6,C7,C9 | C_0805_2012Metric | C15850
1.5uH | L1 | IND_XFL4020-152MEC | C167802
47 | R1,R2,R5,R6,R7,R8,R9 | R_0805_2012Metric | C17414
10k | R3,R4 | R_1206_3216Metric | C17902
RED | D1 | D_0603_1608Metric | C2286
~ | J1 | TerminalBlock_Phoenix_PT-1,5-4-3.5-H_1x04_P3.50mm_Horizontal | C2757925
TPS630701RNMR | U2 | VREG_TPS63070RNMR | C2876599
8P8C_LED_Shielded | J4,J6 | RJ45_Amphenol_RJHSE538X | C386757
22uF | C13,C14,C15,C8 | C_0805_2012Metric | C45783
HeaderP2.54mm | J2 | PinHeader_1x07_P2.54mm_Vertical | C492406
0.1uF | C1,C10,C12,C2,C3,C4 | C_0805_2012Metric | C49678
Screw_Terminal_01x03 | J5 | TerminalBlock_Phoenix_PT-1,5-3-5.0-H_1x03_P5.00mm_Horizontal | C557647
HeaderP2.54mm | J3 | PinHeader_1x06_P2.54mm_Vertical | C706878
L01Z050S05 | IC1 | L01Z050S05

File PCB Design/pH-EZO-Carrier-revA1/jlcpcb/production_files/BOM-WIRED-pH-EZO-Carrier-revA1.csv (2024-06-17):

Comment | Designator | Footprint | LCSC
10uF | C2,C3,C4,C5 | C_0805_2012Metric | C15850
1.5uH | L1 | IND_XFL4020-152MEC | C167802
10K | R3,R4,R5,R6,R7 | R_0805_2012Metric | C17414
10k | R1,R2 | R_1206_3216Metric | C17902
ISO1540 | U3 | SOIC-8_3.9x4.9mm_P1.27mm | C179739
1 uF | C10,C11 | C_1206_3216Metric | C1848
TPS630701RNMR | U1 | VREG_TPS63070RNMR | C2876599
HeaderP2.54mm | J3,J4 | PinHeader_1x03_P2.54mm_Vertical | C2897366
8P8C_LED_Shielded | J1 | RJ45_Amphenol_RJHSE538X | C386757
22uF | C7,C8,C9 | C_0805_2012Metric | C45783
HeaderP2.54mm | J2 | PinHeader_1x07_P2.54mm_Vertical | C492406
0.1uF | C1,C6 | C_0805_2012Metric | C49678
Screw_Terminal_01x02 | J5 | Term_Block_1x2_P5mm | C557646
B0505S-1WR3 | U2 | Converter_DCDC_TRACO_TEA1-xxxx_THT | C7465178

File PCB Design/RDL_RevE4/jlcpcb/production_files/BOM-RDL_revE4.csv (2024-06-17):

Comment | Designator | Footprint | LCSC
CD74HC4051M96 | U2,U4,U6 | SOP-16_3.9x9.9mm_P1.27mm-Edited | C132065
10 uF | C10 | C_1206_3216Metric | C13585
AO3401A | Q1,Q11,Q13,Q16,Q3,Q5,Q7,Q9 | SOT-23-3 | C15127
1.5uH | L1 | IND_XFL4020-152MEC | C167802
10K | R11,R12,R14,R17,R18,R6 | R_0805_2012Metric | C17414
47K | R7 | R_0805_2012Metric | C17713
10k | R1,R10,R2,R3,R4,R8,R9 | R_1206_3216Metric | C17902
1 uF | C9 | C_1206_3216Metric | C1848
AO3400 | Q10,Q12,Q14,Q15,Q2,Q4,Q6,Q8 | SOT-23-3 | C20917
RED | D1,D2 | D_0603_1608Metric | C2286
TPS630701RNMR | U8 | VREG_TPS63070RNMR | C2876599
4 x 10K | RN1 | R_Array_Convex_4x0603 | C29718
PCF8574T | U7,U9 | SOIC127P1032X265-16N_FRED_MODIFIED | C2987288
10k | R5 | R_1206_3216Metric_Pad1.30x1.75mm_HandSolder | C319946
ADS1115IDGS | U5 | TSSOP-10_3x3mm_P0.5mm | C37593
8P8C_LED_Shielded | J7 | RJ45_Amphenol_RJHSE538X | C386757
Screw_Terminal_01x08 | J1,J2 | Term_Block_1x8_P5mm | C395863
Screw_Terminal_01x04 | J3,J5 | Term_Block_1x4_P5mm | C424682
20k | R13,R15,R16,R19,R20,R21 | R_0805_2012Metric | C4328
10uF | C1,C11,C13,C15,C18,C19,C20,C22,C23,C3,C5,C6 | C_0805_2012Metric | C440198
22uF | C24,C25,C27 | C_0805_2012Metric | C45783
0.1uF | C12,C14,C16,C17,C2,C21,C26,C4,C7,C8 | C_0805_2012Metric | C49678
Screw_Terminal_01x12 | J8,J9 | TerminalBlock_Phoenix_PT-1,5-12-5.0-H_1x12_P5.00mm_Horizontal | C5290376
LTC4311CSC6#TRPBF | U3 | SC70-SC6 | C580856
BSS138 | Q17,Q18 | SOT-23-3 | C7420339
Conn_02x15_Top_Bottom | J4,J6 | PinHeader_2x15_P2.54mm_Vertical_Jericho | C7499350
FerriteBead | FB1,FB2 | 0603 | C82155
3V | BAT1 | BatteryHolder_Keystone_3000_1x12mm-Edited | C964818
DS3231SN_T_R | U1 | SOIC127P1032X265-16N | C9866

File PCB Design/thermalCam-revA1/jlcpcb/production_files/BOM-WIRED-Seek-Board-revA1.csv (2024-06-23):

Comment | Designator | Footprint | LCSC
0.01 uF | C1,C2,C3,C4,C5 | C_1206_3216Metric | C13585
10K | R2,R3 | R_0805_2012Metric | C17414
180K | R1 | R_0805_2012Metric | C17713
RED | D1 | D_0603_1608Metric | C2286
8P8C_LED | J2 | RJ45_Amphenol_RJHSE538X | C386757
CH315G | U1 | CH315g-LCSC | C92287
1.5k | R4 | R_0805_2012Metric
Screw_Terminal_01x02 | J3 | Term_Block_1x2_P5mm
59453-051110EDHLF | J4 | AMPHENOL_59453-051110EDHLF

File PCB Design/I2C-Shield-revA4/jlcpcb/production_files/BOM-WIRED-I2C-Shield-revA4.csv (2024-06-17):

Comment | Designator | Footprint | LCSC
TCA9548APWR | U2 | TSSOP-24_W4.40mm | C130026
100K | R8 | R_0805_2012Metric | C149504
AO3401A | Q11,Q13,Q16,Q2,Q3,Q5,Q7,Q9 | SOT-23-3 | C15127
10uF | C1,C2,C5 | C_0805_2012Metric | C15850
10K | R15,R4,R5,R6,R7 | R_0805_2012Metric | C17414
AO3406 | Q1,Q10,Q12,Q14,Q15,Q4,Q6,Q8 | SOT-23-3 | C20917
RED | D1,D2 | D_0603_1608Metric | C2286
PCF8574T | U1,U3 | SOIC127P1032X265-16N | C2987288
RJ45 | J1,J10,J2,J3,J4,J5,J6,J7,J9 | RJ45_Amphenol_54602-x08_Horizontal | C3000197
8P8C_LED | J8 | RJ45_Amphenol_RJHSE538X | C386757
20k | R1,R10,R11,R12,R13,R14,R2,R3,R9 | R_0805_2012Metric | C4328
0.1uF | C3,C4,C6 | C_0805_2012Metric | C49678

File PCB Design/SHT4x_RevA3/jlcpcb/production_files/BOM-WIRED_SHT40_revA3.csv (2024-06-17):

Comment | Designator | Footprint | LCSC
10K | R1,R2,R3,R4,R5 | R_0805_2012Metric | C17414
RED | D1 | D_0603_1608Metric | C2286
5 | J1 | RJ45_Amphenol_54602-x08_Horizontal | C3000197
SHT41I-AD1B-R2 | U2 | SHT4X | C3664410
10uF | C1,C2 | C_0805_2012Metric | C440198
0.1uF | C3 | C_0805_2012Metric | C49678
AP2112K-3.3TRG1 | U1 | SOT95P285X140-5N | C51118
HeaderP2.54mm | J2 | PinHeader_1x05_P2.54mm_Vertical | C706877
BSS138 | Q1,Q2 | SOT-23-3 | C7420339

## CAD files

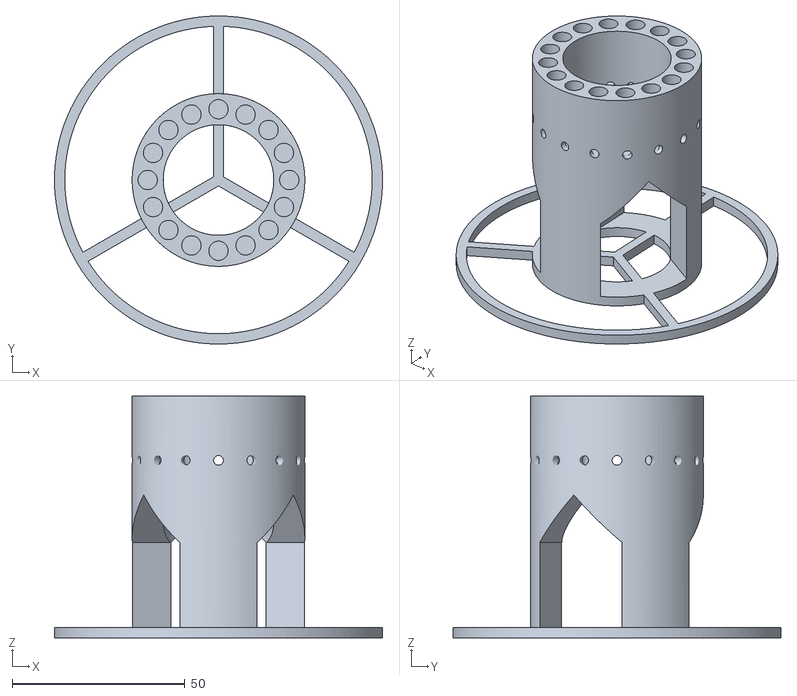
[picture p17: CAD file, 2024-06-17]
3DCAD/ice-bath-device/revB4/ice-bath-device-revB4-Body.stl
95.0 x 95.0 x 70.0

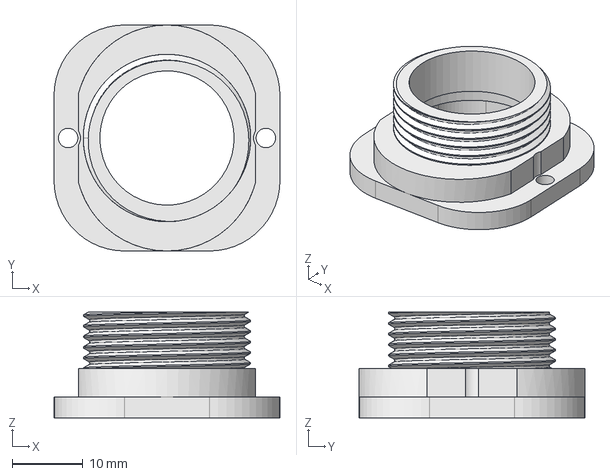
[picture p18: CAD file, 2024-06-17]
3DCAD/ir-cam-adapter/revA2/camera-holder/camera_holder_v10.FCStd
32.0 x 32.0 x 15.0 mm

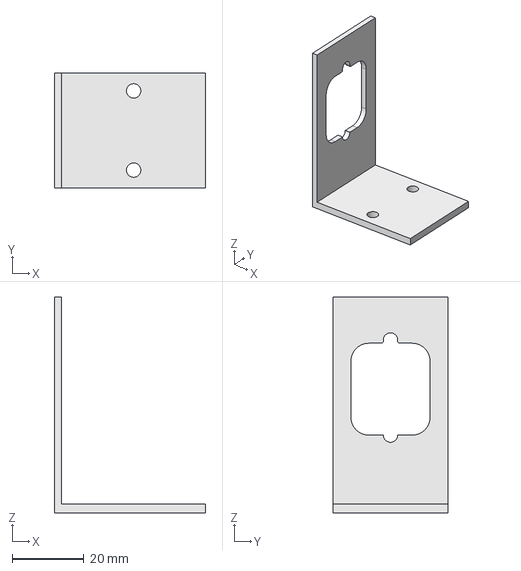
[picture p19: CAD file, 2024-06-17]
3DCAD/ir-cam-adapter/revA2/camera-support-angle/camera_support_angle_v4.FCStd
42.0 x 32.0 x 60.0 mm

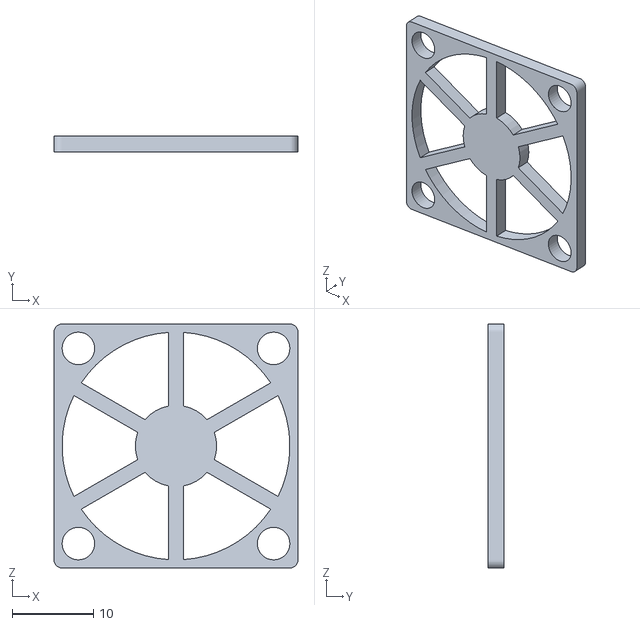
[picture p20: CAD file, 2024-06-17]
3DCAD/orange-pi-fan-grid/revA1/Grid-for-SBC-Fan.STL
30.0 x 2.00 x 30.0

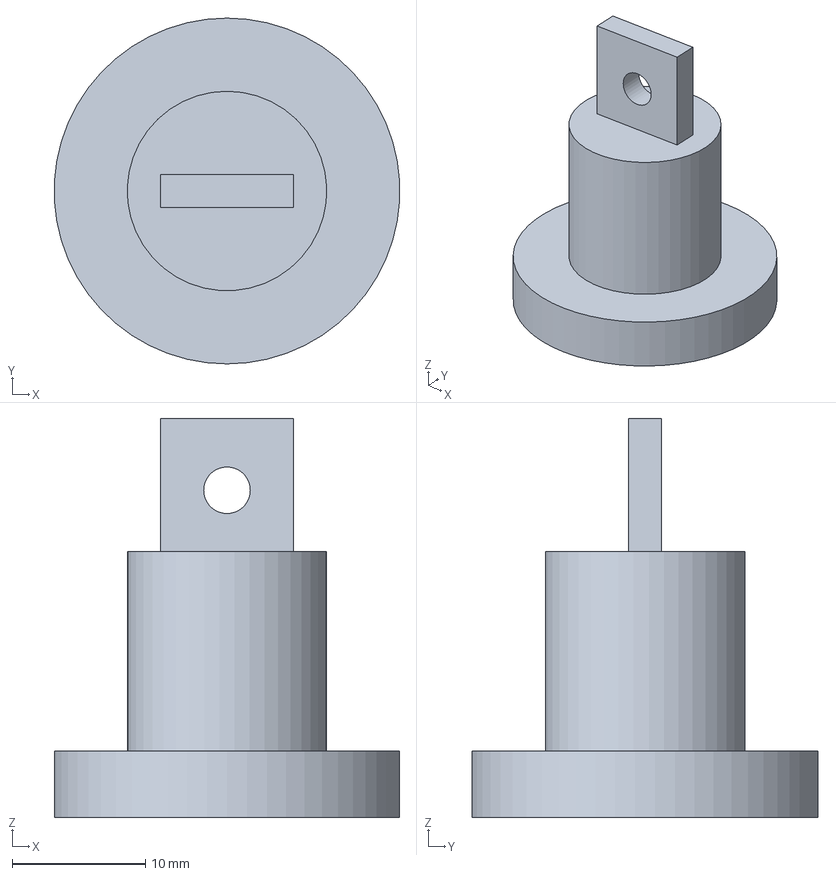
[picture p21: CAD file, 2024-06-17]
3DCAD/radiation-shield/revA1/radiation-shield-adapter-revA1/adapter-for-shield-support.3mf
26.0 x 26.0 x 30.0 mm

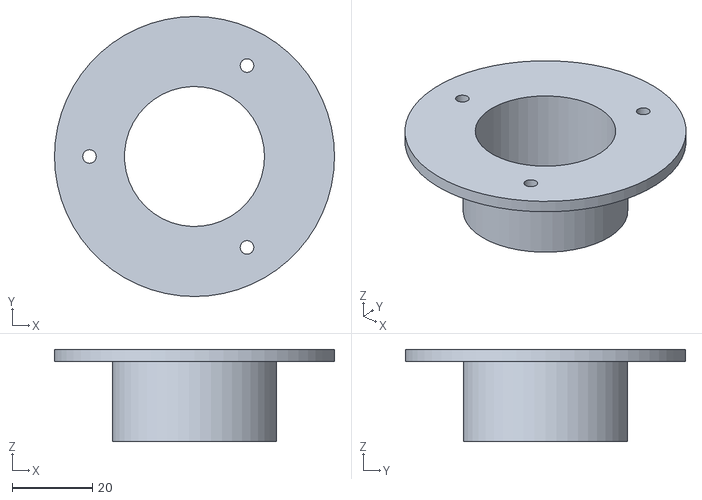
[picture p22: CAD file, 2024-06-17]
3DCAD/radiation-shield/revA1/radiation-shield-original/PipeSupport/PipeSupport.stl
70.0 x 70.0 x 23.0

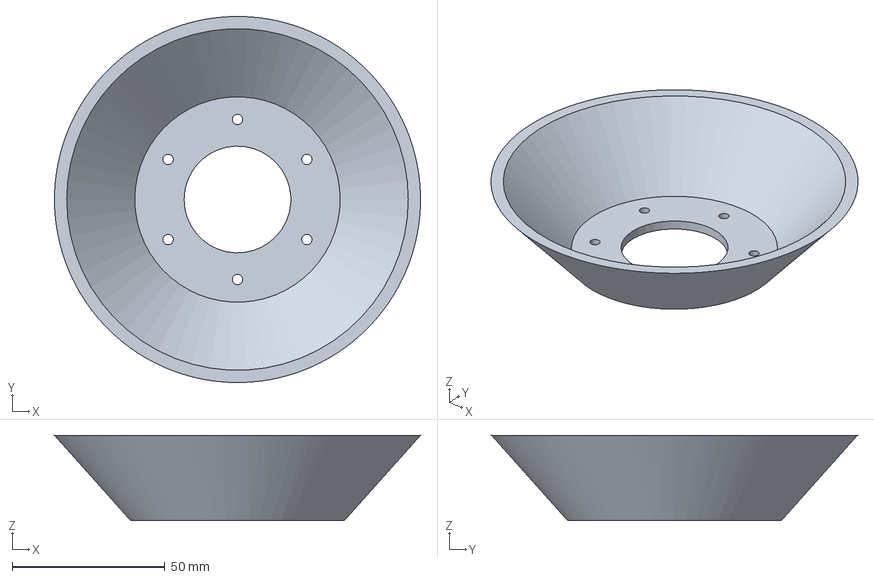
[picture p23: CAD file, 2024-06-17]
3DCAD/radiation-shield/revA1/radiation-shield-original/Plates/Plates.3mf
120.0 x 120.0 x 28.0 mm

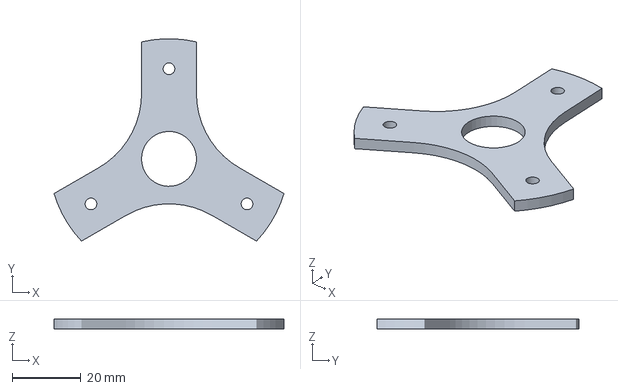
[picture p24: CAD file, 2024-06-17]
3DCAD/radiation-shield/revA1/radiation-shield-original/SensorSupport/SensorSupport.3mf
67.0 x 58.9 x 3.00 mm

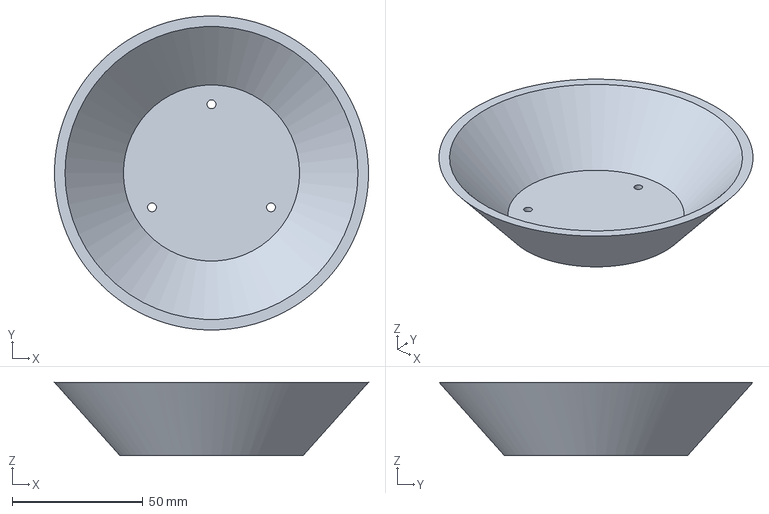
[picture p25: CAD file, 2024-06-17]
3DCAD/radiation-shield/revA1/radiation-shield-original/TopPlate/TopPlate.3mf
120.0 x 120.0 x 28.0 mm

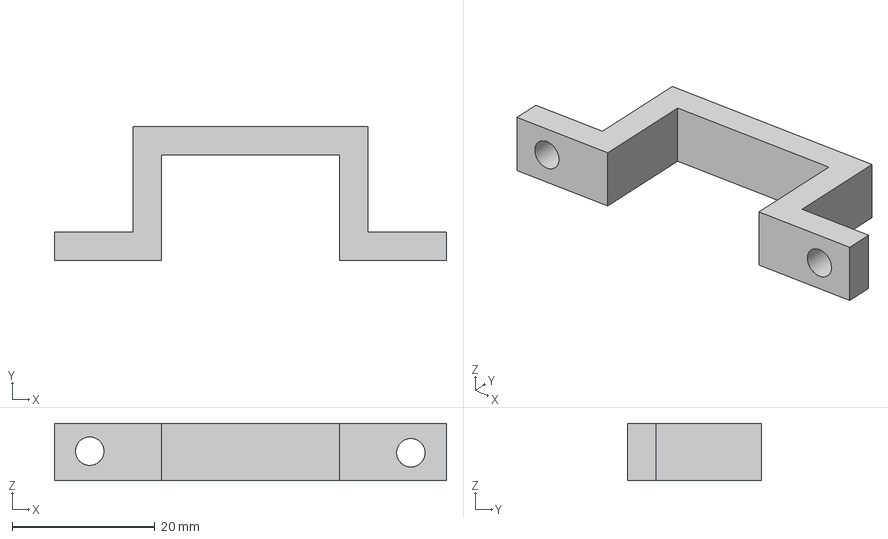
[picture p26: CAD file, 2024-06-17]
3DCAD/usb-hub-bracket/revA1/usb-hub-bracket.3mf
55.0 x 18.8 x 8.00 mm

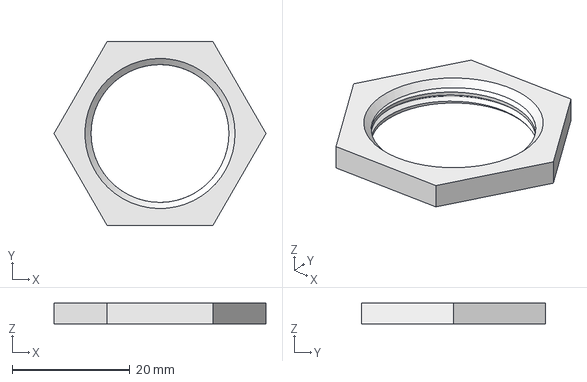
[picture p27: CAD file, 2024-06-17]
3DCAD/ir-cam-adapter/revA2/camera-nut/camera_nut_v6.FCStd
36.0 x 31.2 x 3.50 mm

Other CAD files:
3DCAD/ice-bath-device/revB4/ice-bath-device-revB4.FCStd
3DCAD/ir-cam-adapter/revA2/camera-holder/camera_holder_v10.3mf
3DCAD/ir-cam-adapter/revA2/camera-holder/camera_holder_v10.f3d
3DCAD/ir-cam-adapter/revA2/camera-holder/camera_holder_v10.stl
3DCAD/ir-cam-adapter/revA2/camera-nut/camera_nut_v6.3mf
3DCAD/ir-cam-adapter/revA2/camera-nut/camera_nut_v6.f3d
3DCAD/ir-cam-adapter/revA2/camera-nut/camera_nut_v6.stl
3DCAD/ir-cam-adapter/revA2/camera-support-angle/camera_support_angle_v4.3mf
3DCAD/ir-cam-adapter/revA2/camera-support-angle/camera_support_angle_v4.f3d
3DCAD/ir-cam-adapter/revA2/camera-support-angle/camera_support_angle_v4.stl
3DCAD/radiation-shield/revA1/radiation-shield-adapter-revA1/adapter-for-shield-support.STL
3DCAD/radiation-shield/revA1/radiation-shield-original/Plates/Plates.stl
3DCAD/radiation-shield/revA1/radiation-shield-original/SensorSupport/SensorSupport.stl
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

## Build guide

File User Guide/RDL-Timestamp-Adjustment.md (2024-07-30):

# RTC TIMESTAMP ADJUSTMENT 

To precisely synchronize your Real-Time-Clock (RTC) timestamp with the official time, execute the 
following procedure: 
1. Make sure that your computer clock is synchronized with the official time of your area. 
2. Remove the battery in the battery holder (if any). 
3. Compile and upload the main code to the RDL by using the UPLOAD button in the Arduino IDE 
interface. 
4. Disconnect the USB cable as soon as the upload is complete so that the RTC will experience a power outage.
5. Reconnect the USB cable as soon as possible.
6. The RTC, recognizing that it experienced a power outage, will use the available compile time to update the RTC time.
5. Put in the battery in the battery holder.
6. Time is set.

Note 1: The timestamp error is small (20-30 sec) due to the delay between the start of the compile 
time and the RTC reboot. After that, any reset or upload will not affect the RTC timestamp until the battery is removed or dies. 

Note 2: Make sure that the code is actually recompiled at the time of uploading, so that the code contains the 
current time, and note the time registered at the previous compile. To make sure of that, restart the 
Arduino IDE and change a line of code with a trivial change (like deactivating/activating sensors). 

Note 3: The RTC battery (CR1220) can last years if the RTC experiences very short periods disconnected from the main power (USB cable). However, when in active mode, the RTC drains about 200 uA (micro Amps) on the battery, which will result in a lifetime of a few hundred hours. Therefore, to preserve its energy, the RTC battery should not be left inserted in the RDL when not in use.

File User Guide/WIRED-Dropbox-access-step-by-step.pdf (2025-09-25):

Subject: WIRED: Dropbox access, step-by-step
From: Frederic Coulombe <frederic@jericholab.com>
Date: 2024-08-06, 11:47 a.m.
To: Uzair Jamil <ujamil@uwo.ca>, Nima Asgari <nasgari@uwo.ca> CC: Koami Soulemane Hayibo <khayibo@uwo.ca>

Hi Uzair and Nima,

this is a step-by-step procedure to provide a new user with access to all WIRED data via Dropbox.

1. Provide your Dropbox email address to Frederic.
1. *** This email address must be associated with a Dropbox account.
2. *** If you don't have a Dropbox account, you can create one (free) or login with a Gmail address. In that case, you must provide Frederic with your Gmail email address.
2. Wait for email confirmaon that Frederic sent the invite
3. Go to your inbox or Junk folder and look for an invite email from Dropbox
1.
4. Click on Add to Dropbox

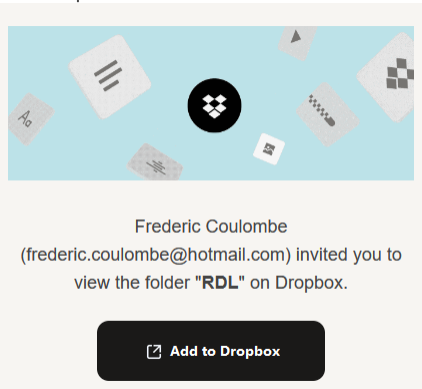
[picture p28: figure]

1.
5. Dropbox will ask to confirm your identy. Login to your personal Dropbox account associated with the email address you provided. (The "I already have an account. Log in." buon is missing from the screenshot).

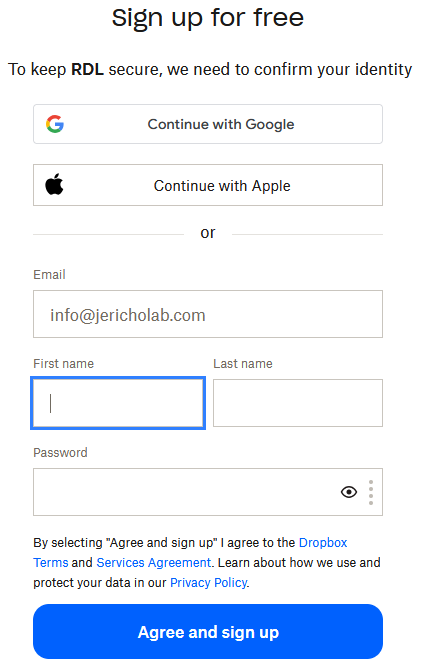
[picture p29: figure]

1.
6. Voila! The WIRED folder has been added to your account.

Note: If you have mulple Gmail addresses, you will have to first log out and log in to the Gmail address associated with WIRED-Dropbox every me you want to access your data. Otherwise, you won't see anything.

If you would prefer to have an easier access, I can also create a 'view only' link that will allow any human being in the world with the link to access your data. This does not require creang a Dropbox account but it provides no privacy to your data. Just let me know your preference as a team.

Thank you,
Best,

Frederic Coulombe, B.Eng., M.Sc.A. CEO and Founder
frederic@jericholab.com
jericholab.com

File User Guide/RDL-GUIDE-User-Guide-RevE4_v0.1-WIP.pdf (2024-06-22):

## USER GUIDE – RESISTANCE DATA LOGGER (RDL) Rev E4 - WIP

### JERICHO LABORATORY INC. - JERICHOLAB.COM

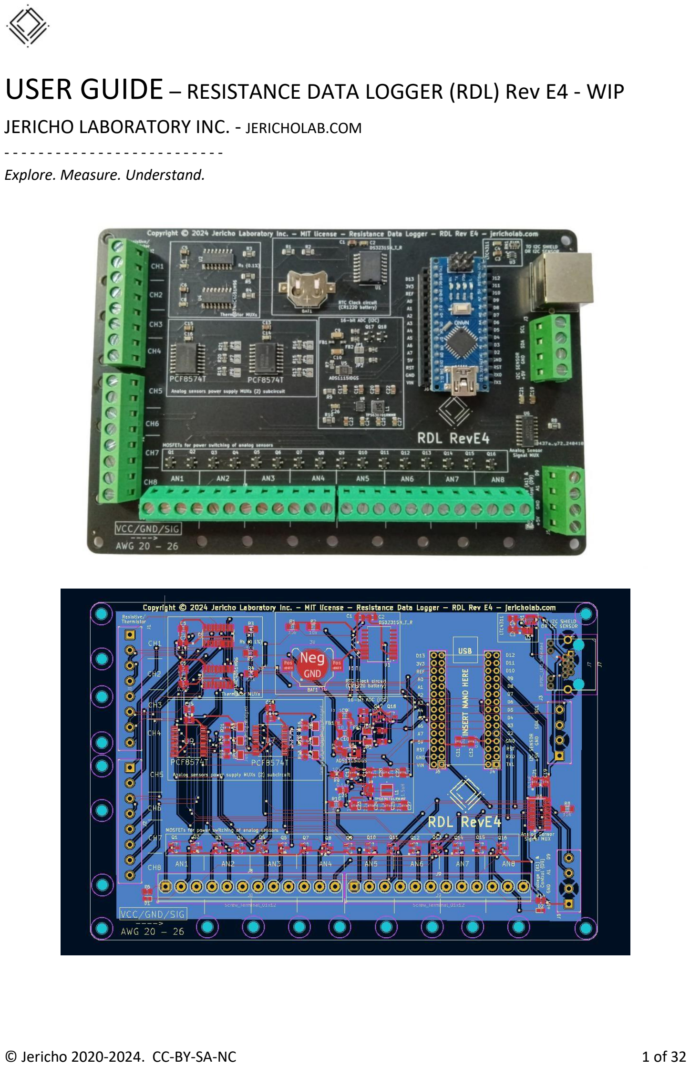
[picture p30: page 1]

© Jericho 2020-2024. CC-BY-SA-NC | 1 of 32
- - - - - - - - - - - - - - - - - - - - - - - - - -Explore. Measure. Understand.

This page is intentionally left blank

### Table of Contents

DISCLAIMER: You are responsible for your own safety. Jericho Laboratory Inc. will not be held responsible for your safety or any damage other than to the device itself. We advise the user to apply great caution while using this product. Always consult an accredited electrician before working with high-voltage electricity. This sensor operates with a low-voltage (5-12V) supply, but other components of your system might require an electrician. Do NOT install in areas prone to thunder as the system has no protection against thunder. It is recommended to NOT open the main enclosure during bad weather (rain, snow, dust) to minimize the risk of component damage and safety issues.

WARNING: This product is neither intended nor warranted for use in following equipment or devices: Special application (such as for medical devices, transportation equipment, traffic signal control equipment, fire and crime prevention equipment, aeronautics and space devices, nuclear power control, fuel control, in vehicle equipment safety devices, and so on) in which extremely high quality and high reliability is required, or if the malfunction or failures of product could be cause for loss of human life, bodily injury.

WARNING: This product contains small parts. Not for children under 5 years old.

### PRODUCT OVERVIEW

Customizable, transparent and well-documented, this product is for those who want to own their data… and their tool.

The Resistance Data Logger (RDL) is a low-cost, ready-to-use, open-source data logger platform for scientists and engineers. Taking its name from the initial ability to measure resistive sensors such as thermistors, the 18-channel device can also measure humidity, luminosity, resistance, voltage, as well as do some basic control. It can communicate with most I2C sensors without additional hardware. Text-based, it focuses on data, providing only elementary graphing capabilities.

Note: For detailed information about the RDL board, please read the “RDL Design Overview” document.

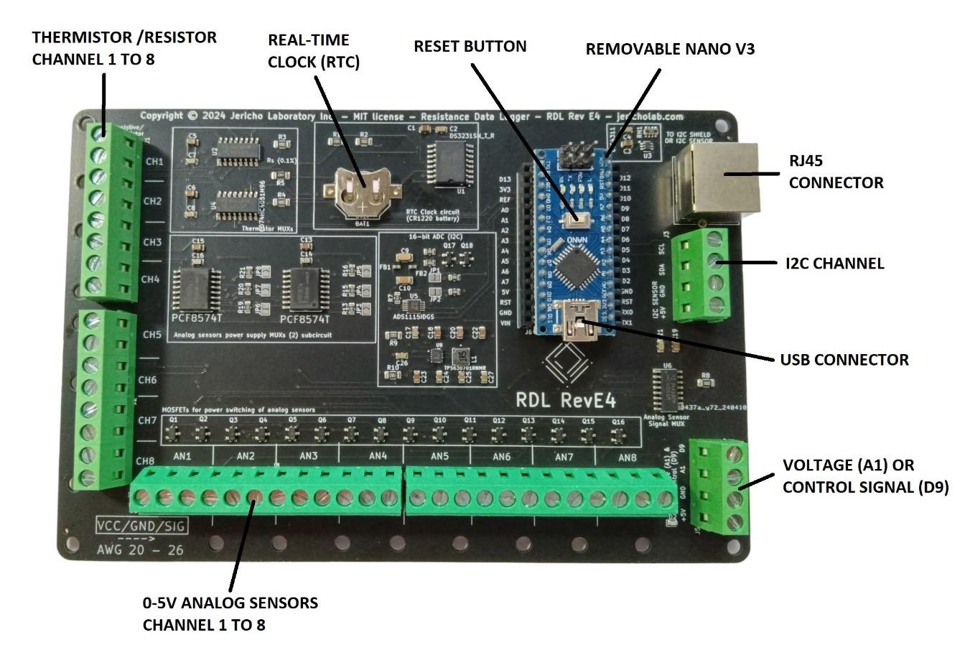
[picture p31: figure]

Figure 1 RDL rev E4 components layout

The RDL can measure a variety of variables over 18 channels. Exact availability of each measurement can be examined in Table 1. Humidity can be read with a digital sensor (I2C) from the SHT family (e.g. SHT4X by Jericho). Other I2C sensors (e.g., accelerometer) can be used by adding the required code. Digital control signals (0-5V, binary or PWM) can also be sent. Resistance measurements allow you to measure a range of phenomena from soil moisture to blood clot formation. Using a low-cost black globe and a wet bulb temperature, the RDL can monitor the comfort via the Wet Bulb Globe Temperature (WBGT) index.

The measured data is sent continuously to your computer, for purposes of display and data storage. The device is equipped with a temperature-adjusted Real-Time clock (RTC) and a 3V battery for accurate and resilient timestamp of the data. The device is compatible with Arduino Nano 3.0 © and its clones. There are many resources to learn about Arduino technology and coding among which the popular book by Jeremy Blum called “Exploring Arduino” (Blum 2019).

IMPORTANT: The RDL is unable to log any data if it is not properly communicating with a PC. Always make sure that the recording is active when using the product.

Table 1 RDL Channels Overview for revision E4

Zone identification | Connector type | Type of channel | Number of channels | Measurement ability | Control ability | Comments
J1, J2 | Screw terminal | Voltage divider subcircuit (A0 or ADS) | 8 | Temperature (Resistor) Resistance Luminosity Soil humidity | N/A | Software signal filtering only. Measurements can be done with Nano ADC (pin A0, 10-bit) or ADS1115 (16-bit). Multiplexed channels.
J8, J9 | Screw terminal | Arduino Analog pins (A1 or ADS) | 8 | Voltage (0-5V) | Digital signal PWM signal (A1 only) | Zone also provides 5V power supply via transistors. For differential voltage measurements, connect the second pin to a ground. Multiplexed channels.
J5 | Screw terminal | Control signal output | 2 | Voltage (0-5V) (if A1 configured as input) | Digital signal PWM signal | D9 pin can output a digital (0/1) signal or PWM signal. A1 can be configured as input or output (digital, not PWM)
J7 | RJ45 (Ethernet) | I2C | 1 | I2C sensors | I2C devices only | Allows connection to Jericho I2C shield(s) or a single I2C slave device.
J3 | Screw terminal | Arduino Analog pins (A4, A5) | 1 | I2C sensors | I2C sensors | SDA = A4, SCL = A5. VCC, GND terminals available. Non-Multiplexed channels.
Nano | Female header | D0, D1 | - | Unavailable | Unavailable | Used to control Rx/Tx
Nano | Female header | D2, D3, D4 | - | Unavailable | Unavailable | Pin used to control thermistor multiplexers (2)
Nano | Female header | D5, D6, D7, D8, D9, D12, D13 | 7 | Available | Available | Digital pins available for temporary circuits
Nano | Female header | D10 | - | Unavailable | Unavailable | Pin used to enable A MUX
Nano | Female header | D11 | - | Unavailable | Unavailable | Pin used to enable T MUX
Nano | Female header | A2, A3, A6, A7 | 4 | Available | Available | 4 analog pins available for temporary circuits

*All analog pins (Ax) can be defined and used as digital pin (Dx). The opposite is not possible.
*Unused pins from the Arduino female headers can be used for user custom features.

PRODUCT FEATURES

- Low-cost portable electrical multi probe data logger
- Designed for scientists, engineers and researchers
- Open-source software and hardware
- Arduino-compatible technology
- Measured variables:
- dry bulb temperature (°C)
- wet bulb temperature (°C), static
- mean radiant temperature (with self-made black globe) (°C)
- electrical resistance (ohm)
- voltage (0 - 5 V)
- illuminance (lux)
- relative humidity (%)
- Wet Bulb Globe Temperature index (WBGT) (thermal comfort index) (°C)
- 20 channels:
- 8 input channels for resistive probes measurements only (e.g. thermistors)
- 2 channels for I2C sensors/devices:
- Examples of commercial I2C devices: air humidity, accelerometer, magnetometer, temperature, pressure, FM transmitter, gyroscope, IR thermal camera, potentiometer, OLED display, current/voltage sensor, gas sensor, FRAM, capacitive sensor, Analog-to-Digital (ADC) converter.
- 8 channels for 0-5 V sensors
- 2 channels for control signals
- Small (TH-1) or large (TH-2) temperature probes available
- Factory-calibrated probes with an overall system accuracy of 0.5°C in the 0-100°C range (3-point calibration)
- Graph capability through a third-party software (e.g., Microsoft Excel®, LibreOffice ®, Python)
- Serial communication with PC (ASCII data)
- Timestamp provided by a Real-Time Clock (RTC) subcircuit (day, month, year, hours, minutes, seconds)
- Data storage, power and communication provided by the PC or Raspberry Pi
- Acquisition rate up to 340 S/s (depending on several factors)
- Free public access to the source code, calibration procedures, application notes
- Made in Canada
- Available on GitHub
- Ready-to-use
- Customizable

### DIGITAL SENSORS AND I2C SHIELD

The RDL is able to communicate with digital sensors that use the standard I2C protocol. Since all sensors use the same single Arduino I2C bus, each sensor must use a different I2C address. This implies that two units of the same sensors cannot be used simultaneously, as they will both “talk” at the same time. You should also verify that each sensor added to the main bus does not have an address that is already used by some of the onboard components. For example, the I2C address of a DS1307 RTC clock is 0x68. Therefore, this address cannot be used by any other sensor.

If the I2C shield is used – and connected – the sensors will be multiplexed both in terms of power and signal, allowing for up to 8 identical devices/sensors to be connected to the system.

The I2C shield is an expansion that connects to the RDL via RJ45 connectors and a very short CAT cable. Each shield adds 8 I2C sensors to the main bus. You must reset the RDL after connecting any I2C device. Otherwise, it will not be detected. Also, if you disconnect an I2C sensor while using the device, you risk jamming the I2C bus, therefore interrupting indefinitely the RDL code. (The chip will keep waiting for an answer from the I2C device.)

For more details, please read the I2C Shield Design Overview.

### REQUIREMENTS

- Computer with minimal hardware:
- CPU: 1 MHz; Memory: 250 MB RAM (Minimum Hardware)
- Internet Access with Internet Explorer 9 or higher
- 1 USB port (2.0 or 3.0)
- Operating system: Windows®7 and newer, Mac OS X®, Linux®, Android® (See details below)
- Wire-stripper for 22 to 28 AWG wire size

### DISPLAY OUTPUT COLUMNS

Order into which the data is printed to the window or text file, from left to right. Each of these columns can be activated/deactivated separately. User judgement must be applied. For example, if asked to do so, the program will calculate and display thermistor temperatures even if no thermistor is connected.

1. Reception Time (HH:MM:SS.MMM) (Arduino IDE Timestamp);
2. Date (YYYY/MM/DD) (RTC Timestamp);
3. Measurement Time (HH:MM:SS) (RTC Timestamp);
4. Data Identification number (i.e. how many measurements done since last reboot);
5. Thermistor temperature (channels 1-8);
6. Resistance values (channels 1-8);

7. Relative humidity values (channels 1-8);
8. I2C sensors readings (demonstration device is AM2301b) (channels 1-2);
9. Voltage readings (channels 1-8);
10. Soil humidity readings (channels 1-8) (Temperature compensated individually);
11. Control signal (0-5V).

### QUICK START: MY FIRST EXPERIMENT USING THE RDL

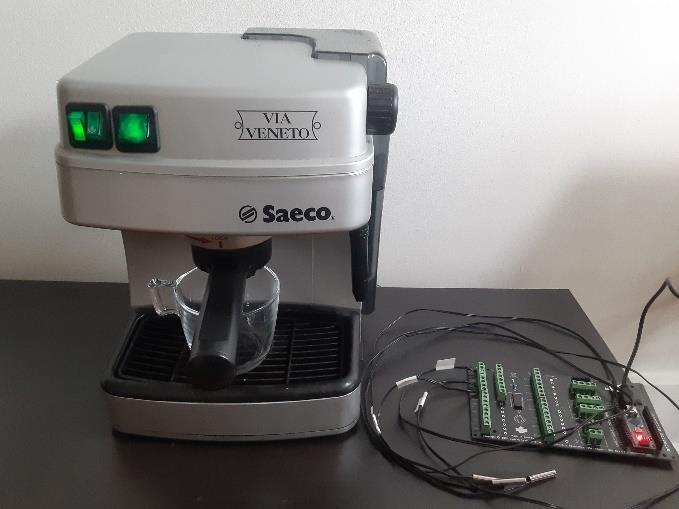
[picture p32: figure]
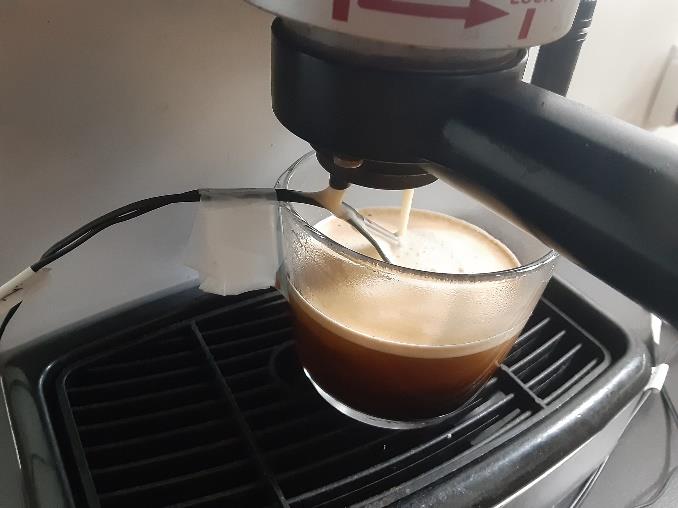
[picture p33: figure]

This procedure will allow you to do a quick basic test of the RDL with the factory settings. It does not require modifying or compiling the source code. This will guide you through some measurements of an espresso machine brewing a cup of coffee. If you do not have access to a coffee machine, you can also use hot water.
Required time: 30 to 90 minutes.
Required material:
- RDL revE4
- 3 thermistors with lead wires
- Access to a computer, an Internet connection and a spreadsheet software (e.g. MS Office, LibreOffice).
- Access to an espresso machine, a cup and scotch tape.

1- Insert a CR1220 battery (3V) in the battery holder of the RDL. The PLUS (+) sign of the battery should be facing up. (No battery is included with the package to reduce shipping restrictions). In the absence of a battery, the clock will not behave properly and might display wrong values.

*To finely synchronize the RTC timestamp with the official time, follow the instructions in the section titled “RTC timestamp adjustment”. This is not required for a first test.

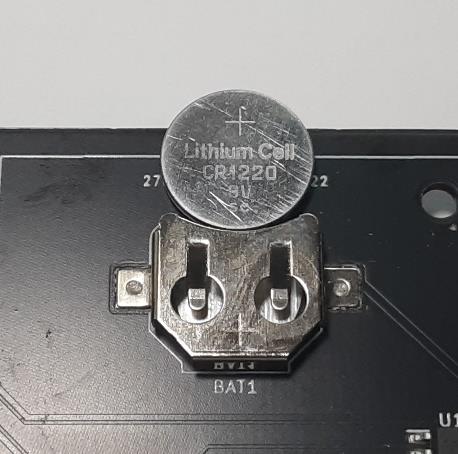
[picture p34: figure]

Figure 2 Inserting the CR1220 battery into the battery holder

2- Connect the USB cable from the RDL to the computer. The PWR (power) red light on the RDL should light up.

3- If this is not already the case, connect each required thermistor to its dedicated channel with the provided screwdriver. For this quick test, three probes are required. Other probes can remain connected without problems. Thermistors have no polarity, so you can invert the two wires without consequence. Make sure that the thermistor ID is coherent with the channel in the source code (see Error! Reference source not found.). Make sure that the terminal contact is solid by pulling slightly on each wire. If using extension wire, the wire gauge should be AWG26 or larger to ensure a solid and easy connection to screw terminals. Smaller gauge can be difficult to use. The silkscreen indicates the wire gauges that are acceptable (i.e. AWG 20-26).

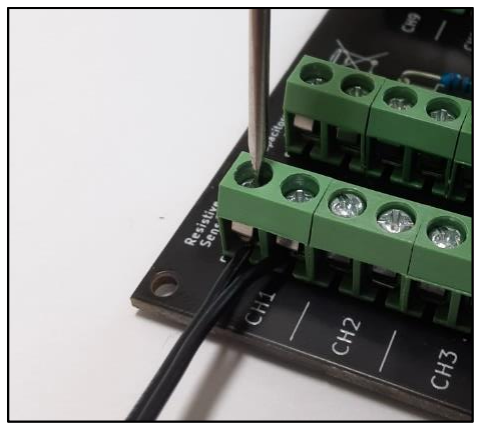
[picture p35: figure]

Figure 3 Connecting the thermistor probe wires to the dedicated channel C1

4- Download the free Arduino Software IDE for your operating system on the Arduino official website (www.arduino.cc). Follow the instructions provided by the website. Since the Arduino IDE 2.0 is fairly recent, we recommend using the legacy version (1.8.19) for now. It is also easier to follow along our guide.

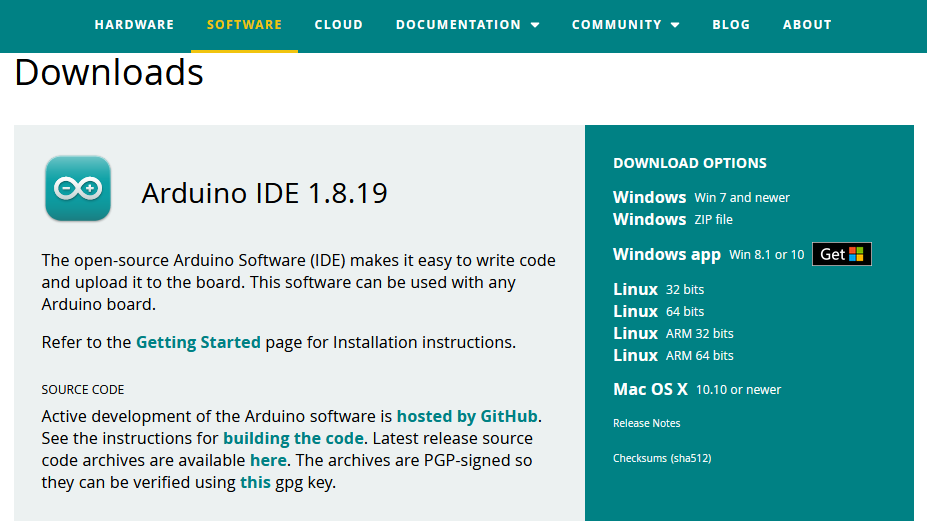
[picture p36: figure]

Figure 4 Arduino official website software download section

5- Launch the IDE software. We suggest temporarily using the English version to easily follow the User Guide instructions. The software launches in your operating system default language, but you can modify this in File/Preferences/Editor Language. You will need to restart the software.

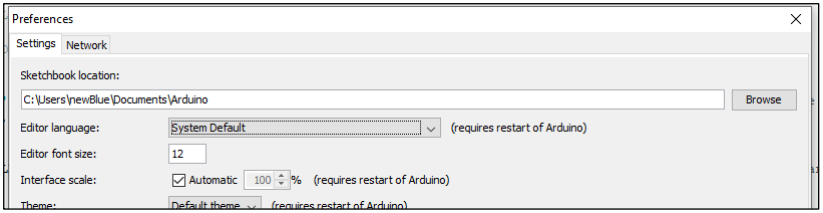
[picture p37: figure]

6- Modify the configuration settings. Go to Menu -> Tools.
a. Board -> Arduino Nano
b. Processor -> ATMega328P (Do not choose “Old Bootloader” as this will generate an uploading error)
c. Port -> COM4. The exact port name might vary depending on your system. (e.g., ttyUSB1, ttyUSB2, COM1, etc.) You can disconnect/reconnect the USB cable to see which port name appears when you connect the RDL.

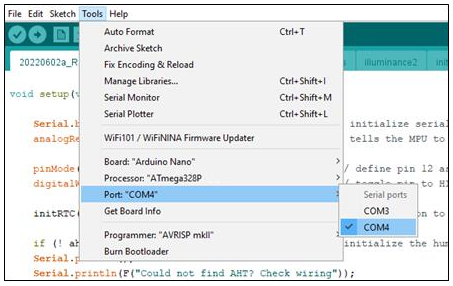
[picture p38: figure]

Figure 5 Serial port selection through the Arduino IDE menu

7- Go to Menu -> Tools -> Serial Monitor. A new window should pop-up. At first, the data being displayed on your screen will be gibberish, because the baud rate (i.e., communication rate) is wrong (default is 9600).

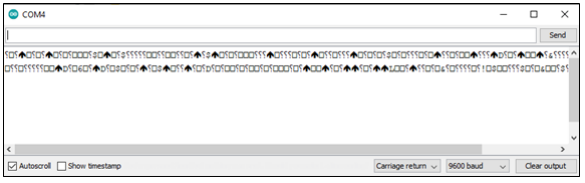
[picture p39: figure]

Figure 6 Example of gibberish data coming in due to a mismatch of the baud rates

8- The baud rate inside the RDL source code should match the baud rate of the computer. On the bottom right of the Serial Monitor window, set the baud rate to 57600 (program default is 9600). Once the baud rate is correct, readable data will start coming in through the Serial Monitor. It is suggested to ‘CLEAR OUTPUT’ with button of the same name to keep the window clean when comes the time to copy/paste.

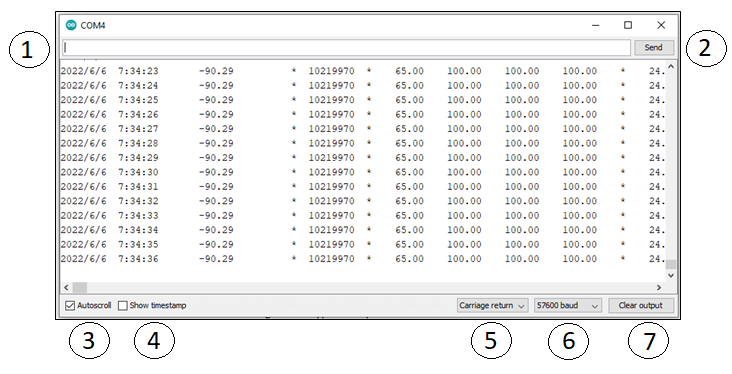
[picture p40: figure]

Figure 7 Serial Monitor window components. 1) Command line; 2) Send command button; 3) Activate/Deactivate autoscroll;
4) Show/Hide timestamp; 5) Selection of the end of line symbol; 6) Selection of the baud rate; 7) Clear the window.

9- Select the ‘Carriage return’ in the End of line options (item 5 in Figure 7). Otherwise, the command will not be recognized by the RDL.
10- The default factory setting for the acquisition rate is 1 Hz (i.e., 1000 milliseconds interval). You can modify it to 2000 ms or leave it at 1000 ms. To modify that value, you must enter the text “INTERVAL” in the command line (item 1 in Figure 7).
11- If there are too many columns, you can zoom out by using CTRL + the mouse wheel. ‘Autoscroll’ can be deactivated to look at the data.

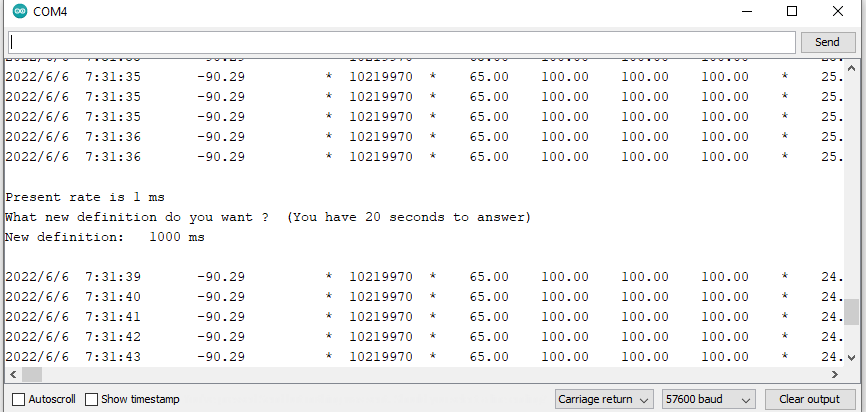
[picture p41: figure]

Figure 8 Example of an interval modification from 1 to 1000 ms through the command line

12- Before starting your experiment, you can clear the window by clicking on “Clear output” in the bottom right of the window (item 5 in Figure 7). Otherwise, non-relevant data can be erased later during post-treatment.
13- You can now proceed with your experiment. Meanwhile, using adhesive tape, position the three probes in the following way.
a. Probe C1: Near the liquid exit to measure the temperature of the coffee outflow;
b. Probe C2: Near the bottom of the cup, without touching the bottom surface, if possible. This will allow measuring the global temperature of the coffee accumulated in the cup.
c. Probe C3: In the center of the top surface of the espresso machine. This surface becomes hot during the warm-up and operation phase since the boiler is right beneath the surface. It can be interesting to see how its temperature evolves over time.
14- Prepare the coffee as usual, and turn on the machine to preheat. Wait until the temperatures stabilize on your screen before activating the compressor (brewing phase).

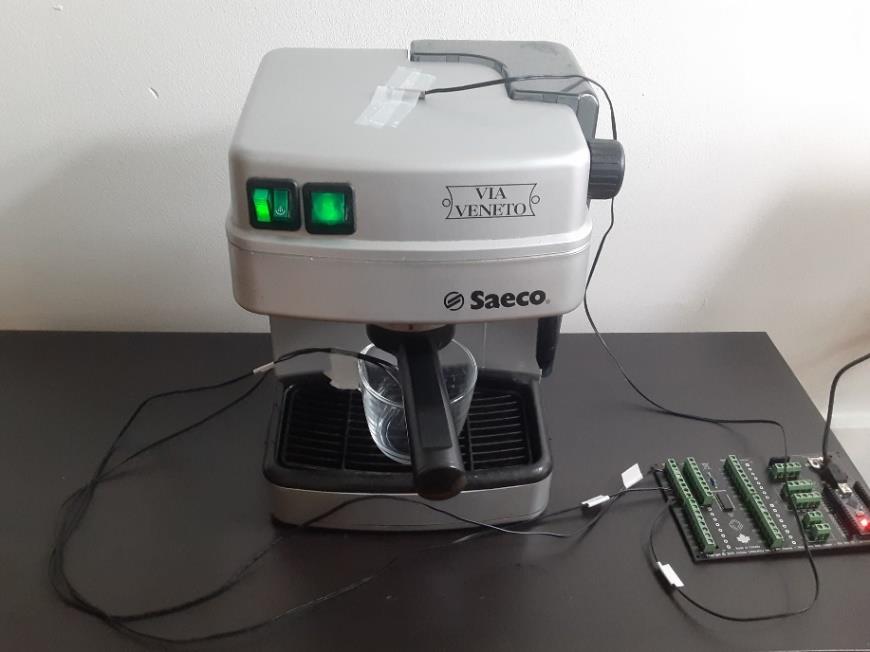
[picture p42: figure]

Figure 9 Caption

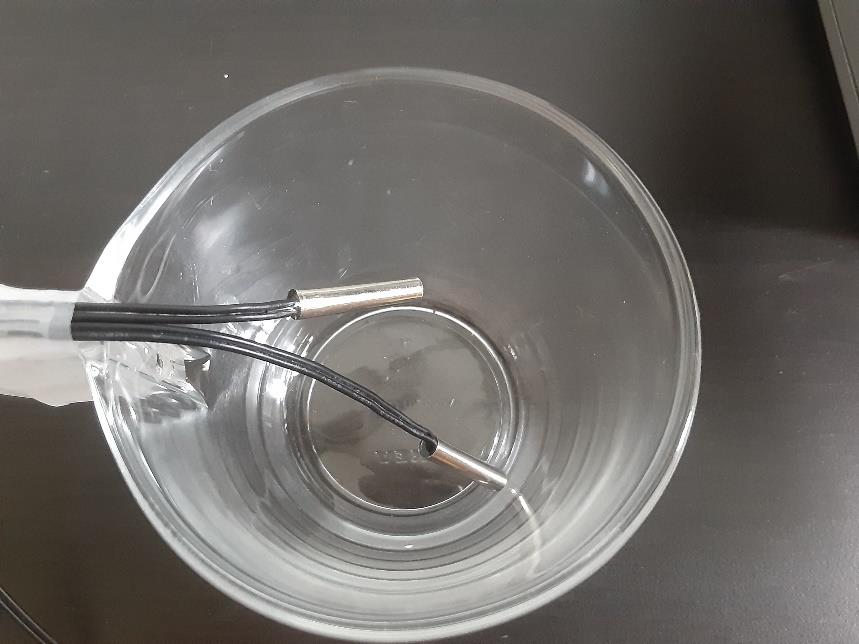
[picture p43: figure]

Figure 10 Position of the two probes inside the empty cup

15- As the experiment unfolds, watch the data accumulate in the Serial Monitor window. Each time, the RDL sends data, the light ‘TX’ on the controller should blink very quickly.
16- When you have gathered all your data, untick the case ‘Autoscroll’. This will prevent the screen from moving while you select your data. Do not close your Serial Monitor window until you have saved your data in another reliable location.
17- Press “CTRL + A” to select all text. Then copy by pressing “CTRL + C”.
18- Open a text editor and paste all text by pressing “CTRL + V”.

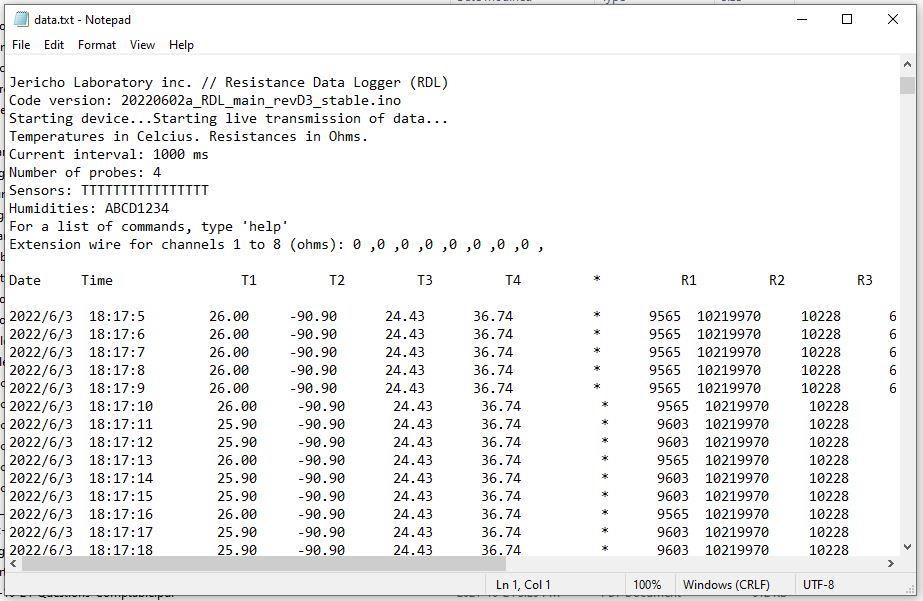
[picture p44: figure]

Figure 11 RDL text file output sample

19- Save the text file on your Desktop (ex: test_1.txt). This is an important step, since the data within the Serial Monitor is not recorded permanently. Data is lost when the window closes. 20- Open Microsoft Excel or, alternatively, a free spreadsheet software (e.g., LibreOffice Calc).
21- Go to Menu -> Data -> From text. Select the text file. In some recent versions of Microsoft Office, you might have to activate “Legacy Wizards” in order to have access to data import from a text file. If this is your case, follow Microsoft instructions on the topic on their forum.

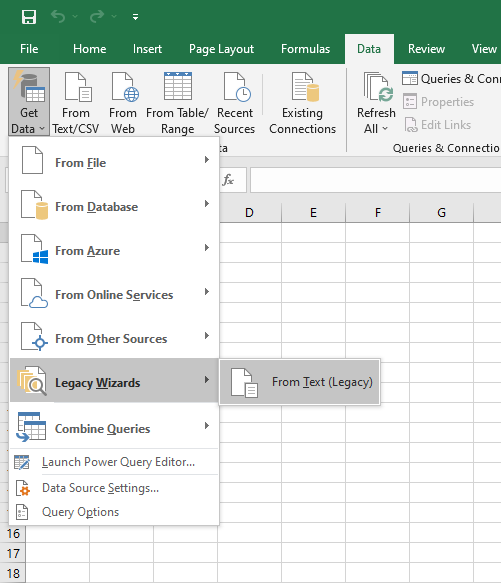
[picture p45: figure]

Figure 12 Microsoft Excel menu for the Text Data Import

22- Select the ‘Delimited’ data type.

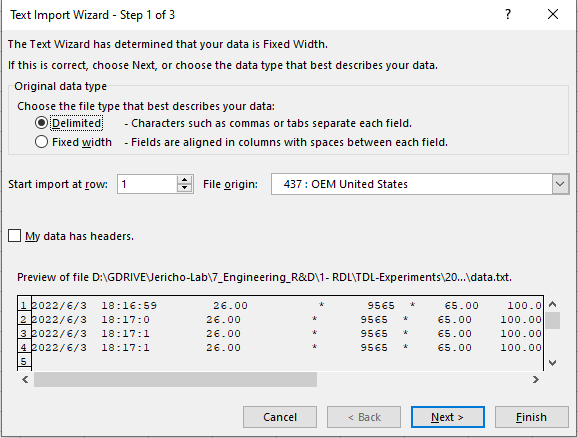
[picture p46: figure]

23- Select the ‘space’ character as the delimiter. Tick the box ‘Treat consecutive delimiters as one’. Click Finish.

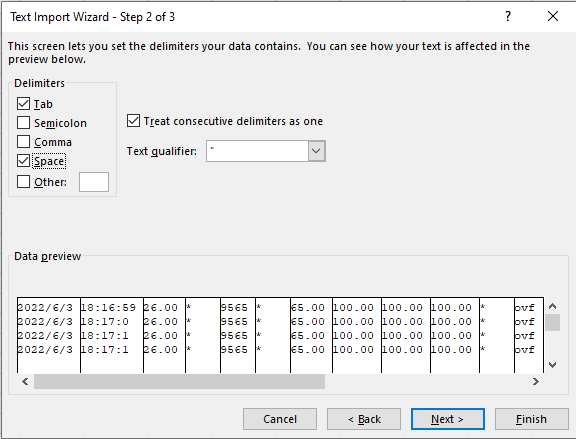
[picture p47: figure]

24- Import data to ‘Existing Worksheet’.

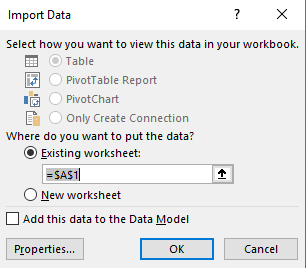
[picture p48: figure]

25- If necessary, adjust the ‘timestamp’ column cell format to ‘Short Date’ in order to display the time properly.
26- You can now create various graphs from your data. For example, you might create a “Line graph” with the column ‘Time’ as the x-axis and three temperatures as the y-axis. In our case, we decided to put data from channel C4 on a secondary vertical axis.

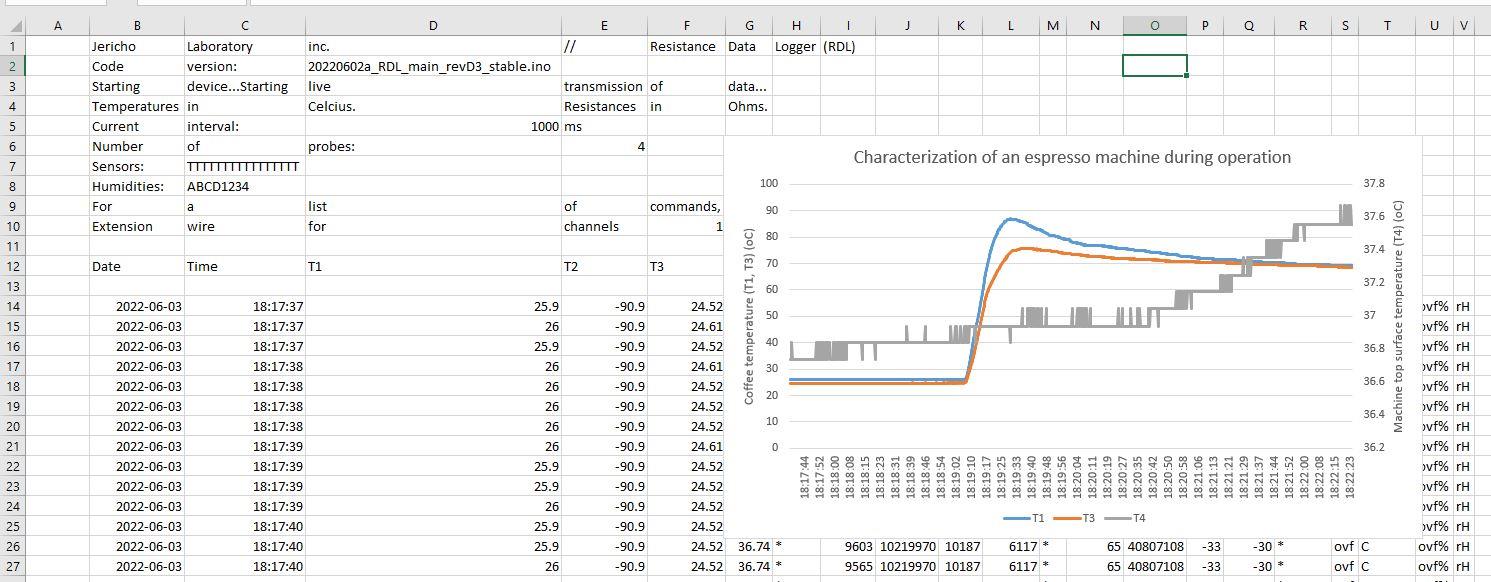
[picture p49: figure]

Figure 13 Data treatment inside Microsoft Excel

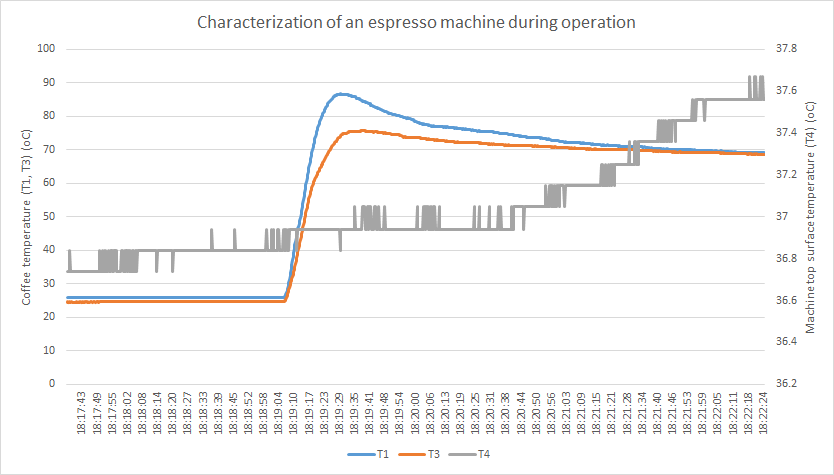
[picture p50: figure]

Figure 14 Example of data post-treatment with MS Excel ® for the espresso machine experiment

27- Analyzing the data is the final and most interesting part of the experiment. First, it is good practice to analyze the quality of the data. Are there any surprises, irregularities, noise in the data? Second, what are the trends that we observe in the data (peaks, valleys, plateau, oscillations, etc.)? Here are a few examples for the espresso machine graph.
d. The temperature of the coffee outflow sensor increased very fast initially. Due to the thermal inertia of the large sensor, it is not clear at what time the coffee temperature outflow really peaked. It would be interesting to rerun the experiment with a small probe, which has lower inertia. If the curve does not change, that would suggest that probe inertia does not play a significant role on this specific aspect.
e. Both coffee temperature sensors peaked before the end of the brewing. Since we know that the brewing lasted around 30 seconds, we can confirm that the heater element is not powerful enough to maintain the maximum temperature of the water. The maximum heating power [watts], the coffee grain thermal inertia and the water reservoir temperature are likely to play a role in the curve of the coffee temperature.
f. There seems to be a slight inflexion point around 18:20:06. This could be the time at which the brewing stopped. We could improve our observation by plotting a first order time derivative of the data for C1 and C3. It would be easier to see if our eye is being misled. That could be confirmed with a second experiment which measures the start and stop of the compressor. This could be measured in one of several ways: manually with a clock, with a current sensor, or with a digital switch.

g. The two sensors eventually converged to a very similar temperature. This is likely to indicate that after a few seconds without liquid inflow, the stratification became negligible due to conduction and convection within the cup.
h. There was very little change in the temperature of the top surface (less than a degree). This was a surprising result as one could expect that the incoming cold water from the reservoir would have had some effect on the machine casing temperature. Also, with the help of the secondary axis, we can see that much of the temperature increase happened after the brewing. This challenges our understanding of the espresso machine.
i. The top surface temperature had not peaked when the experiment ended. It would be interesting to run the experiment longer for that reason.

As you can see, much can be learned from a single graph. A first experiment often leads to a series of more refined experiments.
28- We advise you to keep the original data (i.e., text file) in case you eventually want to restart your analysis from scratch for a variety of reasons.

### RDL FACTORY SETTINGS

Factory settings are the settings active when you first receive your device. Most of the RDL capacities are active in order to easily demonstrate every aspect of the product. The factory settings are a combination of memory parameters and source code parameters. You can alter the factory settings by combining serial commands and small source code alterations. You can always go back to factory settings by using the command “EEPROM-ERASE”.

Factory settings (EEPROM section)

- Acquisition interval: 1000 mS
- Number of probes: 16
- Temperature unit: Celsius

Factory settings (source code section)

- Time display: Yes
- ID display: Yes
- Temperature display: Yes
- Resistance display: Yes
- I2C display: Yes
- Voltage reading display: Yes
- Soil humidity display: Yes
- Wet Bulb Globe Temperature (WBGT) display: Yes
- Steinhart-Hart thermistor coefficients (A,B,C):
- For the Starter Kit package

- Channels C1 to C8: Custom coefficients specific to included thermistor probes
- Channels C9 to C16: Generic coefficients for 10k NTC thermistor
- For the Controller-only package
- Channels C1 to C16: Generic coefficients for 10k NTC thermistor

### AVAILABLE SERIAL COMMANDS

In order to interact with the RDL, the user must type in some of the following keywords at the top of the ‘Serial Monitor’ window and then click ‘Send’. The option ‘Carriage return’ must be selected for the RDL to detect the command. The commands are not case-sensitive.

HELP: The command ‘HELP’ prints out the available serial commands: “CELCIUS, FAHRENHEIT, KELVIN, RESET, EEPROM-ERASE, INTERVAL, QTY-T, QTY-V, I2CSCAN”. Activity will resume after a few seconds.

INTERVAL: The command ‘INTERVAL’ allows adjusting the measurement interval (i.e., acquisition rate). The same rate applies to all sensors. After receiving the command, the program will wait for the user to enter a value between 1 and 96 400 000 ms (i.e., 24 h). Enter the value ‘1’ to force maximum speed, which will vary depending on the number of active probes. The default factory value is 1000 ms (1 second).

The maximum acquisition rate depends on a combination of factors:
- amount of sensors/values/data printed per poll
- baud rate (source code default is 57600, but the Nano can reach 115200)
- RTC use (DS3231MZ performance degrades above 57600)
- Speed of the PC or Raspberry Pi (buffer overload)

Note: For intervals shorter than 1000 ms, we recommend activating the serial monitor native timestamp, which includes milliseconds. Otherwise, all datapoints taken within the same second will receive the same timestamp from the RTC (hh:mm:ss), which can be problematic for plotting time series afterwards. You can keep the RTC timestamp though, as the native timestamp does not include the date.

QTY-T: The command ‘QTY-T tells the device how many thermistor channels must be active. Value must be between 1 and 8. The lowest channels value are activated first (e.g. A value of 3 will activate channels 1 to 3). The parameter is stored in the permanent memory and will be remembered after a shutdown or reset of the device. A quantity of eight (8) probes is the default factory setting. No confirmation or further instructions are required. Operation will resume after a few seconds.

QTY-V: The command ‘QTY-V tells the device how many voltage measurement channels must be active. Value must be between 1 and 8. The lowest channels value are activated first (e.g. A value of 3 will activate channels 1 to 3). The parameter is stored in the permanent memory and will be remembered after a shutdown or reset of the device. A quantity of eight (8) probes is the default factory setting. No confirmation or further instructions are required. Operation will resume after a few seconds.

CELSIUS: The command ‘CELSIUS’ tells the device to display temperatures in Celsius (°C) units. Unit is stored in the permanent memory (EEPROM) and will be remembered after a shutdown or reset of the device. Celsius is the default factory setting. No confirmation or further instructions are required. Operation will resume after a few seconds.

FAHRENHEIT: Display temperature in Fahrenheit (°F) units. No confirmation or further instructions are required. Operation will resume after a few seconds.

KELVIN: Display temperatures in Kelvin (K) units. No confirmation or further instructions are required. Operation will resume after a few seconds.

I2CSCAN: Scan each of the eight (8) I2C channels from the I2C shield. For each channel, the command will print out the I2C addresses for which a device has been found. If a device is connected on the main hub (not multiplex), it will appear in all each channel.

EEPROM-ERASE: Erase the EEPROM memory and return to the factory settings (RATE 1000 ms, Celsius units, all 16 channels active, etc.). No confirmation or further instructions required. Operation will resume after a few seconds.

RESET: This command restarts the microcontroller. It is the equivalent of pressing the RESET button on the Arduino Nano. This is convenient to print out the header when starting a clean measurement session for logging purposes. Operation will resume after a few seconds.

### IMPORTANT USER PARAMETERS

Most variables within the source code should not be modified by the user during normal operations, but some important parameters are not available through the serial commands and need be modified within the source code before uploading it to the microcontroller. These parameters are located at the top of the main file.

Among the following list, each parameter that contains the word ‘display’ can be activated (1) or deactivated (0) by giving it a value of 1 or 0. Parameters that are not measured are not displayed, and vice-versa.

- Header Display (headerDisplay)
- This parameter controls the display of the columns headers, which is adapted to the currently active parameters and sensors.

- Time display (timeDisplay)
- The Real-Time Clock allows the RDL to keep track of the date and time with high accuracy. The RTC clock is polled at every cycle and its data is printed out in the serial monitor. This is especially useful for experiments that last more than 24 hours since most Serial Monitor Data Logging software do not keep track of the date. The RTC poses a restriction however in the maximal speed that the RDL can operate (approximately 5 Hz).
- Identification Number display (idDisplay)
- By default, the source code attributes an identification number to each measurement (i.e., 1, 2, 3, etc.) The ID can supplement or substitute the timestamps in some cases, such as high-speed measurements. It is also useful during post-treatment to keep track of the data continuity (i.e., lines 2450 to 2460 are missing due to bad data)
- Temperature display (tDisplay)
- Activate or deactivate the display of temperature measurements. Deactivating the temperature display can be useful when the user is not using the multiplexed channels or is not using them with thermistors or photoresistors. In that latter case, the user might only activate the display of the resistance values.
- Resistance display (ohmDisplay)
- Activate or deactivate the display of the resistance value for the multiplexed channels. Deactivating the resistance display can be useful in cases where the user is not using the multiplexed channels or is only interested in temperatures. The resistance and temperature values can be displayed independently.
- pH reading display (phDisplay)
- Activate or deactivate the display of pH measurements.
- Strain measurements display (strainDisplay)
- Activate or deactivate the display of strain measurements.
- Air humidity display (SHT40Display)
- Activate or deactivate the calculations and display of relative humidity via SHT4x sensors.
- Current sensor display (currentDisplay)
- This parameter controls the display of current sensor values. By default, the current sensor value will try to add temperature compensation. However, if the parameter tDisplay is deactivated, the function will use 0°C as a temperature compensation, which will add a significant bias to the current sensor values.
- Soil humidity sensor display (terosDisplay)
- This parameter controls the display of soil humidity sensor values (Teros 10).
- Voltage display (voltDisplay)
- Activate or deactivate the measurement, calculation and display of the voltage input in the corresponding channels (0-5V, DC current).

Parameters for controlling the active channels

The following parameters allows the selection of channels which contain an I2C sensor for each type.

- Active channels for SHT40 measurements (i2cChannels_sht40)
- Active channels for strain measurements (i2cChannels_strain)
- Active channels for pH measurements (i2cChannels_ph)
- Active channels for electrical current measurements (channels_current)

For example, the following line “int i2cChannels_strain[] = {1,4};” will tell the RDL that channels 1 and 4 contain a strain measurement sensor (NAU7802). To deactivate the readings, you can either leave an empty list (i.e. {}) or deactivate the measurement altogether (e.g. “strainDisplay = 0”) Note that the channels are numbered from 1 to 8. Do not use the value 0. It is also possible to use the same channel with multiple sensor types. This could occur with NAU7802 (two functions) or daisy chains (two sensors on the same channel).

### HOW TO MODIFY AND UPLOAD THE SOURCE CODE TO THE RDL

The RDL already comes ready-to-use, but you might want to make some changes to the source code or use the latest release.

1- If this is not already done, do steps 1 to 6 inclusively from the Quick Start section.
2- Download the latest source code on the Github repo (main branch).
3- Copy the files to your working directory. The folder name should be the same as the main file without the file extension (e.g., 20220602a_RDL_main_revD3_stable)
4- Open this code file with the Arduino IDE software. (File -> Open)
5- Make the desired modifications to the code.
6- Make sure that the code can compile. Go to Menu -> Sketch -> Compile.

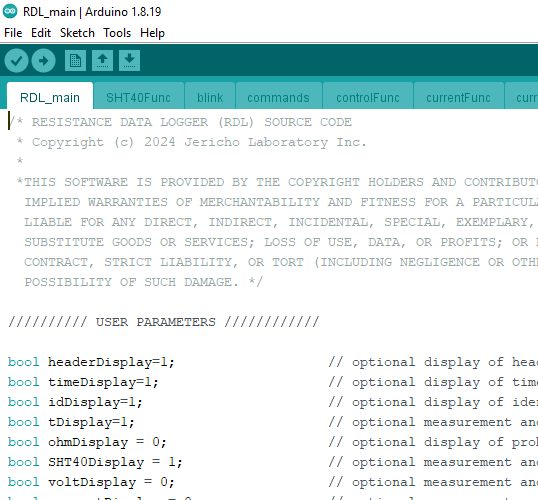
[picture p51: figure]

Figure 15 Example of the source code opened inside the Legacy Arduino IDE software

7- Connect the RDL to the computer via the USB cable.
8- Make sure that the proper USB port is selected by the software.
9- Install the required libraries listed below. This only has to be done once on each computer. Go to Menu -> Manage Libraries. This is necessary even if you don’t plan on using some of the features (e.g., I2C humidity sensors) due to their presence in the source code, even when the features are not activated. EEPROM.h and Wire.h are included in the source code but is not required to install since it is native to the IDE software.
a. RTClib.h by Adafruit
b. SparkFun_Qwiic_Scale_NAU7802_Arduino_Library.h
c. Adafruit_SHT4x.h
d. Adafruit_ADS1X15.h
e. Adafruit_PCF8574.h

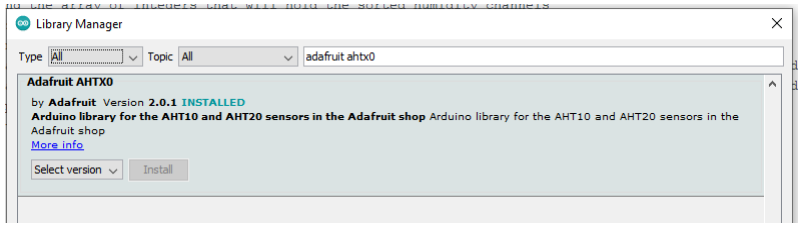
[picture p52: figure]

Figure 16 Searching the Adafruit AHTX0 library within the Arduino IDE Library Manager

10- Go to Menu -> Sketch -> Upload. This will compile then immediately upload the code to the RDL. The “RX” and “TX” LED light should flash quickly while the code is being uploaded. Normal upload time should be 10 seconds. Normal compile time should 10 to 15 seconds. Total time should then be 20 to 25 seconds.
11- Follow the steps from the Quick Start guide to open the Serial Monitor and see if you get the expected results.

For more help about Arduino coding and debugging, visit the official forum on arduino.cc or ask your local community: the Arduino platform is very common worldwide.

### HOW TO LOG DATA TO FILE

The Arduino IDE can hold large quantities of data inside the serial monitor window. However, this data is kept in memory temporarily, and eventually the data would have to be copied manually to a text file for permanent storage. There is always a chance that the computer or program would shut down before doing that operation. It is therefore best to save data as we go to a text file. There are two preferred ways to log the data, depending on your needs.

1) Run Python scripts (Compatible with all OS)
2) Setup Services/Daemons (Compatible with Linux only for now)

Python scripts can run on all platforms that have Python 3 interpreter and the required packages installed. The following two scripts are available:

- WIRED-logging-RDL-USB0.py (Continuously logging incoming RDL data to a text file)
- WIRED-syncing.py (Continuously syncing files to Dropbox account)

Note that the syncing script is also able to sync the data from the WIRED project, which includes thermal and surveillance cameras. These two devices each have their own Python Script.

A shell script (WIRED-runAll.sh) is able to launch all Python scripts. This mode however is not resilient to failure and reboots. You must start the scripts manually each time.

Services, also called “Daemons” in the Linux environment, are the most resilient way to log data from the RDL. When set up, they will make sure that each Python script is launched at each startup and will try to execute again in case of crash or interruption.

Important: Whatever the method chosen, it is important that the computer does not sleep. When going to sleep (e.g., closing the lid) the data logging is interrupted. The USB voltage supply is maintained but the serial communication is interrupted.

For detailed information about the use of these methods, please read the WIRED Python Scripts Design Overview and the WIRED Daemons Design Overview.

### NOISE CONTROL

Electromagnetic (EM) noise control is an important part of signal measurements. The amount of noise present depends on several factors among which the prevalence of EM noise in the environment and the length of the sensor lead wire. Long lead wires – several meters - tend to act as antennas and are likely to pick up strong EM noise even in low noise environment such as a typical home.

No hardware filter is used in Revision E4. Experiments have shown that hardware filters like RC filters are not well suited to multiplexed measurement channels. Since the multiplexer only polls each channel for a limited amount time, the condensator needs time to equilibrate each time. Software filters are preferred instead.

A software filtering is simpler to implement than hardware filtering: it consists of modifying the value for the parameter ‘NUMSAMPLES’ in the source code. For maximum speed, use value of 1. For heavy filtering, you can use values of 5 to 20. Since the Nano ADC takes 15 ms per reading, a value of 20 would delay by at least 300 ms per channel. For 16 channels, that would mean a delay of 4800 ms, without accounting for the processing time (i.e., arithmetic averaging). This would limit your ability to gather data at a faster interval than 5s.

### OPEN-SOURCE LICENSES

Jericho Laboratory operates the RDL suite of products with the following open-source licenses: SOFTWARE: GPL 2.0
HARDWARE: MIT
WEBSITE, DOCUMENTS: Creative Commons CC-BY-NC-SA (Non-commercial use only)

For more information about the user permissions and responsibilities associated with each license, please refer to our website or contact us via email at info@jericholab.com.

### CONTACT

For more information, tutorials, FAQ, software updates, accessories and replacement parts, please visit us at jericholab.com. We also appreciate you sending comments and suggestions at info@jericholab.com.

### ABOUT JERICHO LAB

Jericho is a company based in Montreal, Canada. Our mission is to improve access to scientific equipment by providing provide low-cost high-quality products to students, scientists and engineers. The Rose of Jericho (Anastatica hierochuntica) is a desert plant that can survive death by desiccation (absence of water).

### ABOUT ARDUINO ©

The RDL is compatible with the Arduino language, which is based on the ‘Processing 3’ language, which itself is similar to the C language. Most of the C/C++ core language can be used with the RDL device and the Arduino IDE software. You can create classes, use inheritance, composition, and other functionalities, but STL and exceptions cannot be used. Arduino first appeared around 2005 and is now used worldwide by over a million users. Jericho is not endorsed nor linked in any sense with the Arduino company. Arduino clones are produced by hundreds of manufacturers around the world, with different level of qualities.

Please do not throw away this product to garbage or recycle bin as it can contain toxic substances and/or heavy metals. Please send your Jericho product to your local electronic waste drop-off site so that it can be disposed of properly.

### FREQUENTLY ASKED QUESTIONS (FAQ)

- What is a thermistor?
A thermistor is a tiny passive device which has an electrical resistance that varies with the temperature of its material. It is a word play with the words ‘thermal’ and ‘resistor’.
- Can I use the RDL to do something else?
Yes, you can modify the product, software and hardware to add or remove capabilities. However, any physical modification of the device will void the warranty.
- I dropped the RDL in the water, what should I do?
Water will create short-circuits that will render the device unusable temporarily. Put it in dry uncooked rice with closed container for 24 to 48h to remove humidity, like you would do for a smartphone. It should work again.
- What other software than Arduino Software can I use to control the RDL device?
The IDE software provided by Arduino is specifically designed for Arduino and Arduino-compatible devices and provides an easy interface to beginners and advanced users. However, some users might prefer to use more professional programming tools. A free option that is often recommended is the software Atom, combined with the Platformio add-on.
- I broke some component. How do I find replacement parts?
You can consult the Bill of Material (BOM) to find the exact part number and order a new part online. If you believe this is due to a manufacturing defect and you are still covered by your warranty, contact us by email.
- Should I tin the wire endings to be used with screw terminals?
No, NASA procedures for example require to NOT thin the wires due to different thermal expansion coefficients of the wire and solder.
- How can I modify the column title that is being printed out? For example, how can I print units “g/mm3” beside the word ‘soil’?
In the source code, you can modify the column title in the function “printHeader”. You would change the String content from “soil” to “soil [g/mm3]”.

### TROUBLESHOOTING

- Error: “An error occurred while uploading the sketch. (avrdude: stk500_getsync() attempt 10 of 10: not in sync: resp=0x31)
- This can happen when the RDL was busy sending sensor data when the PC tried to communicate. It happens more often after a change of USB port.
- Try reuploading the program.
- Try to press once the RESET button on the Nano during the upload phase of the Arduino IDE.
- Try disconnecting the USB cable and reconnecting, then reuploading.
- Try another USB port of the PC.
- Try to restart the program.
- Error: “Board at COM4 is unavailable.”
- The selected serial port is not detecting the RDL/Arduino.
- Verify that the USB cable is connected to both the PC and the RDL.
- Verify that the corresponding port is selected in the Arduino menu.
- The printed output of a channel makes no sense. Example, the temperature of the channel C2 is -273.15°C.
- Negative, random-looking values are usually associated with empty or opened channels (false contact, broken probe). Verify that there really is a sensor connected to the channel and that the connection is solid.
- Error: “Variable X was not declared in this scope”
- Two very common reasons for this error is 1) a function was indeed declared at the wrong place 2) a missing bracket or semi-colon has created a complete fuckup of the entire code. It can be hard to find the exact spot. Undo the latest change or go back to your previous working saved version.
- “My Arduino has stopped responding to ‘uploads’ via the Arduino IDE”
- In case the Nano stops responding, you can try to reinstall the bootloader. This kind of error can happen if a code upload has been interrupted. The bootloader is a very small program that allows the Nano to communicate and receive a script. To reinstall the bootloader, follow the instructions here: https://docs.arduino.cc/built-in-examples/arduino-isp/ArduinoISP. (https://docs.arduino.cc/built-in-examples/arduino-isp/ArduinoISP)

### USEFUL REFERENCES

- Arduino Uno Rev3, Digikey, https://media.digikey.com/pdf/Data%20Sheets/Arduino%20PDFs/A000066_Web.pdf
- ATmega 328p datasheet: http://ww1.microchip.com/downloads/en/DeviceDoc/Atmel-7810-Automotive-Microcontrollers-ATmega328P_Datasheet.pdf (http://ww1.microchip.com/downloads/en/DeviceDoc/Atmel-7810-Automotive-Microcontrollers-ATmega328P_Datasheet.pdf)
- Free Arduino tutorials, https://www.tutorialspoint.com/arduino/
- Blum, Jeremy. 2019. Exploring Arduino: Tools and Techniques for Engineering Wizardry. John Wiley & Sons.
- Learn: Basic knowledge about principles and techniques behind the Arduino ecosystem. https://docs.arduino.cc/learn
- Build your own data logger (free course with videos). FreakLabs: Hardware for conservation. https://freaklabs.org/learn/build-your-own-data-logger/overview/

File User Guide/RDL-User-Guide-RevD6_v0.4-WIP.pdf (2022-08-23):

## USER GUIDE – RESISTANCE DATA LOGGER (RDL) Rev D6 - WIP

### JERICHO LABORATORY INC. - JERICHOLAB.COM

© Jericho 2020-2022. CC-BY-SA-NC | 1 of 45
- - - - - - - - - - - - - - - - - - - - - - - - - -Explore. Measure. Understand.

This page is intentionally left blank

### Table of Contents

WARNING: This product contains small parts. Not for children under 5 years old.
WARNING: This product is not intended for critical use, internal use, medical use or food safety.
WARNING: One item of the Starter kit contains cadmium (photoresistor), which is a toxic substance. Cadmium is a forbidden substance in the European Union.
DISCLAIMER: Jericho Laboratory Inc. will not be held responsible for your safety or any damage other than to the device itself. We advise the user to apply great caution while using this product.

### PRODUCT OVERVIEW

The Resistance Data Logger (RDL) is a low-cost, ready-to-use, open-source data logger for scientists and engineers. Mostly centered around high-quality temperature measurements, the 20-channel device can also measure humidity, luminosity, resistance, voltage, as well as do some basic control. Text-based, it focuses on data, providing only elementary graphing capabilities.

Customizable, transparent and well-documented, this product is for those who want to own their data, but also own their tool.

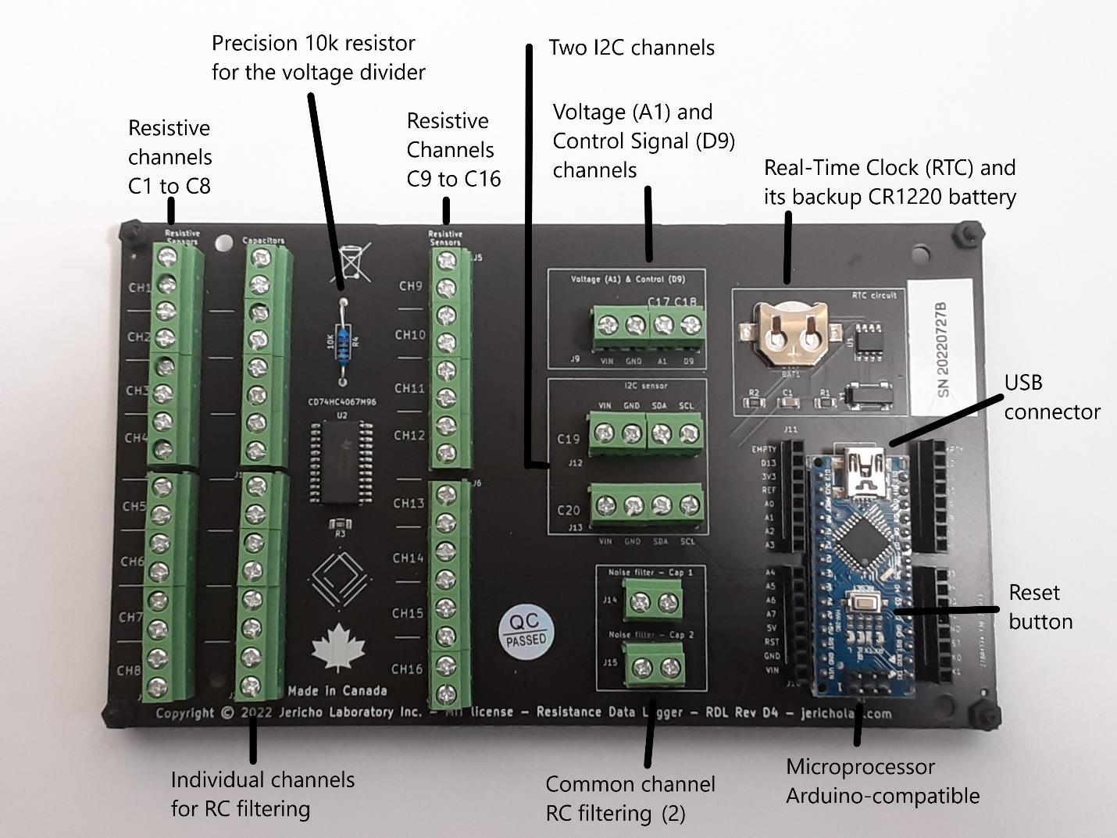
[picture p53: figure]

Figure 1 RDL rev D6 components layout

The RDL can measure a variety of variables over 20 channels, simultaneously. Exact availability of each measurement can be examined in Table 1. Humidity readings can be done natively with the use of wet bulbs. Humidity can also be read with a digital sensor (I2C) from the AHX family. Other I2C sensors (e.g., accelerometer) can be used by adding the required code. Digital control signals (0-5V, binary or PWM) can also be sent. Resistance measurements allow you to measure a range of phenomena from soil moisture to blood clot formation. Using our low-cost black globe and a wet bulb temperature, the RDL can monitor the comfort with the Wet Bulb Globe Temperature (WBGT) index.

The measured data is sent continuously to your computer or smartphone, for purposes of display and data storage. The device is equipped with an RTC clock and a 3V battery for accurate and resilient timestamp of the data. The device is compatible with Arduino Nano 3.0 ©.

IMPORTANT: The RDL is unable to log any data if it is not properly communicating with a PC or smartphone. Always make sure that the recording is active when using the product.

Table 1 RDL Channels Overview for revision D6

Zone identification | Connector type | Type of channel | Number of channels | Measurement ability | Control ability | Comments
J1, J2, J3, J4 | Screw terminal | Voltage divider subcircuit (A0) | 16 | Temperature (resistor) Resistance Luminosity Soil humidity | N/A | Optional condensator can be connected in zones J5, J6
J9 | Screw terminal | Arduino Analog pin (A1) | 1 | Voltage (0-5V) | Digital signal | For differential voltage measurements, connect the second pin to a ground.
J9 | Screw terminal | Arduino Digital pin (D9) | 1 | N/A | Digital signal PWM signal
J12, J13 | Screw terminal | Arduino Analog pins (A4, A5) | 2 | I2C sensors | i2c sensors | SDA = A4, SCL = A5. VCC, GND terminals available nearby Already talking to to RTC clock address
J14, J15 | Screw terminal | Filter | 2 | N/A | N/A | Can accommodate two condensators in parallel with the voltage divider analog input for noise filtering purposes.
Nano | Female header | D0, D1 | 2 | Unavailable | Unavailable | Used to control Rx/Tx pins
Nano | Female header | D2, D3, D4, D5 | 4 | Unavailable | Unavailable | Pin used to control multiplexer
Nano | Female header | D7, D8, D10, D11 | 5 | Available | Available | 5 digital pins available for temporary circuits
Nano | Female header | D12 | 1 | Unavailable | Unavailable | Pin used to supply voltage to components
Nano | Female header | D13 | 1 | Unavailable | Unavailable | Pin used to supply voltage to components. Can be used but also connected to the board LED.
Nano | Female header | A2, A3, A6, A7 | 4 | Available | Available | 5 analog pins available for temporary circuits

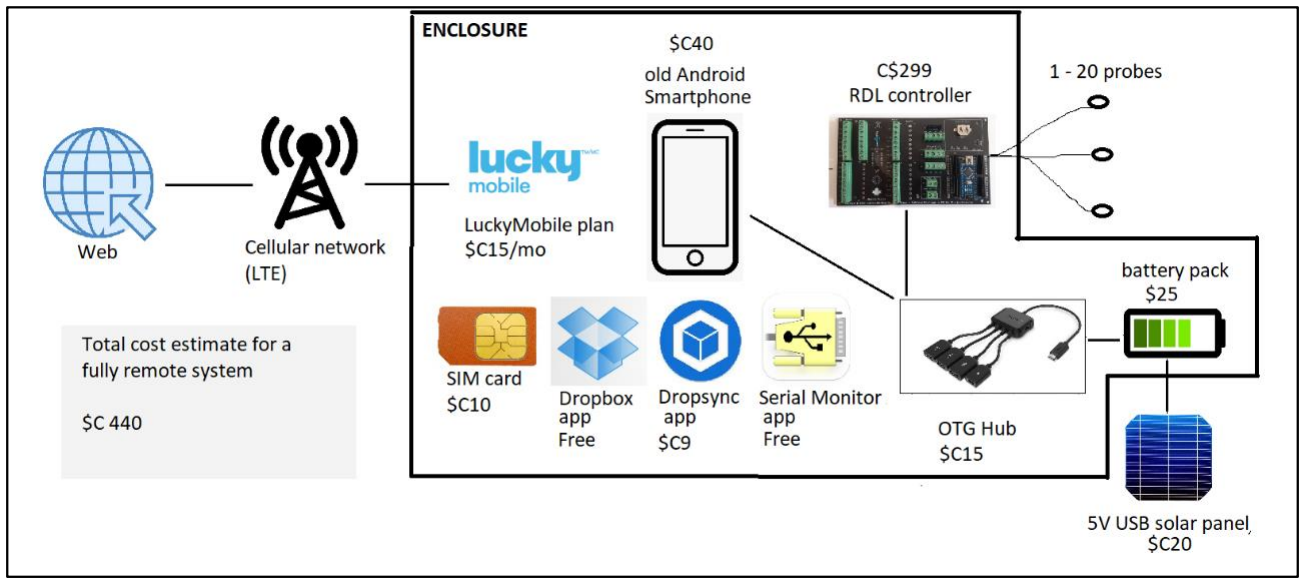
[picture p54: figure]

Figure 2 Fully autonomous RDL system components overview

PRODUCT FEATURES

- Low-cost portable electrical resistance multi probe data logger
- Designed for scientists, engineers and researchers
- Open-source software and hardware
- Arduino-compatible technology
- Measured variables:
- dry bulb temperature (°C)
- wet bulb temperature (°C), static
- mean radiant temperature (with self-made black globe) (°C)
- electrical resistance (ohm)
- voltage (0 - 5 V)
- illuminance (lux)
- relative humidity (%)
- Wet Bulb Globe Temperature index (WBGT) (thermal comfort index) (°C)
- 20 channels:
- 16 input channels for resistive probes measurements only
- 2 channels for I2C sensors
- 1 channel for 0-5 V sensors
- 1 channel for control signals
- Small (TH-1) or large (TH-2) temperature probes available
- 8 thermistor probes, calibrated, included in the Starter kit
- Factory-calibrated probes with an overall system accuracy of 0.5°C in the 0-100°C range (3-point calibration)

- Graph capability through a third-party software (e.g., Microsoft Excel®, LibreOffice ®, Python)
- Weatherproof case (inspired by NEMA Type 3 requirements)
- Waterproof probes (inspired by NEMA Type 6P requirements)
- Serial communication with PC/smartphone (ASCII data)
- Timestamp provided by a Real-Time Clock (RTC) subcircuit (day, month, year, hours, minutes, seconds)
- Data storage, power and communication provided by the PC/smartphone
- Acquisition rate up to 340 S/s (depending on many factors)
- Free access to the source code, calibration procedures, application notes
- Made in Canada
- Available on GitHub
- Ready-to-use
- Customizable

### PRODUCT DESIGN AND CODE OVERVIEW

For more information about the product design choices, code architecture, calibration methodology and other topics, please consult the document titled “Product design and code overview”, available in the documentation section of our website (upcoming).

### REQUIREMENTS

- Computer with minimal hardware:
- CPU: 1 MHz; Memory: 250 MB RAM (Minimum Hardware)
- Internet Access with Internet Explorer 9 or higher
- 1 USB port (2.0 or 3.0)
- Operating system: Windows®7 and newer, Mac OS X®, Linux®, Android® (See details below)
- If using with a smartphone, it must have “host capability” and be used with an OTG USB hub (not included)
- Wire-stripper for 22 to 28 AWG wire size

### DISPLAY OUTPUT COLUMNS

Order into which the data is printed to the window or text file, from left to right. Each of these columns can be activated/deactivated separately. User judgement must be applied. For example, if asked to do so, the program will calculate and display thermistor temperatures even if no thermistor is connected.

1. Time (HH:MM:SS.MMM) (Arduino IDE Timestamp);
2. Date (YYYY/MM/DD) (RTC Timestamp);
3. Time (HH:MM:SS) (RTC Timestamp);
4. Identification (ID) number;
5. Thermistor temperature (channels 1-16);
6. Resistance values (channels 1-16);
7. Relative humidity values (channels 1-16);
8. I2C sensors readings (demonstration device is AM2301b) (channels 1-2);
9. Voltage readings (channels 1-2);
10. Luminosity readings (channels 1-16);
11. Soil humidity readings (channels 1-8) (Temperature compensated individually);
12. Wet Bulb Globe Temperature (WBGT) readings (Comfort index);
13. Control signal (0-5V).

### QUICK START: MY FIRST EXPERIMENT USING THE RDL

This procedure will allow you to do a quick basic test of the RDL with the factory settings. It does not require modifying or compiling the source code. This will guide you through some measurements of an espresso machine brewing a cup of coffee. If you do not have access to a coffee machine, you can also use hot water.
Required time: 30 to 90 minutes.
Required material:
- Starter kit
- Access to a computer, an Internet connection and a spreadsheet software (e.g. MS Office, LibreOffice).
- Access to an espresso machine or hot water, and a cup.

Warning: DISCLAIMER: Jericho Laboratory Inc. will not be held responsible for your safety or any damage other than to the device itself. Be careful when manipulating hot liquids.

1- Get the RDL Starter Kit items out of the box.

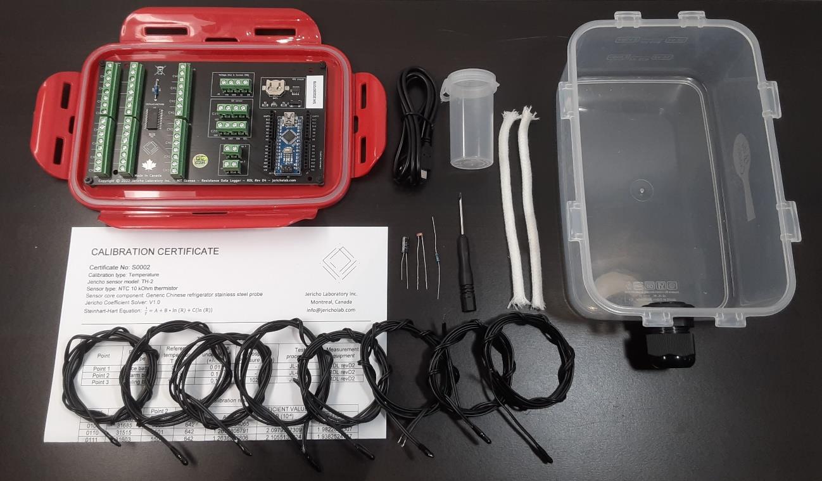
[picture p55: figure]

Figure 3 Content of the Starter Kit rev D6

2- Insert a CR1220 battery (3V) in the battery holder of the RDL. The PLUS (+) sign of the battery should be facing up. (No battery is included with the package to reduce shipping restrictions). In the absence of a battery, the clock will not behave properly and might display wrong values.

*To finely synchronize the RTC timestamp with the official time, follow the instructions in the section titled “RTC timestamp adjustment”. This is not required for a first test.

Figure 4 Inserting the CR1220 battery into the battery holder

3- Connect the USB cable from the RDL to the computer. The PWR (power) red light on the RDL should light up.

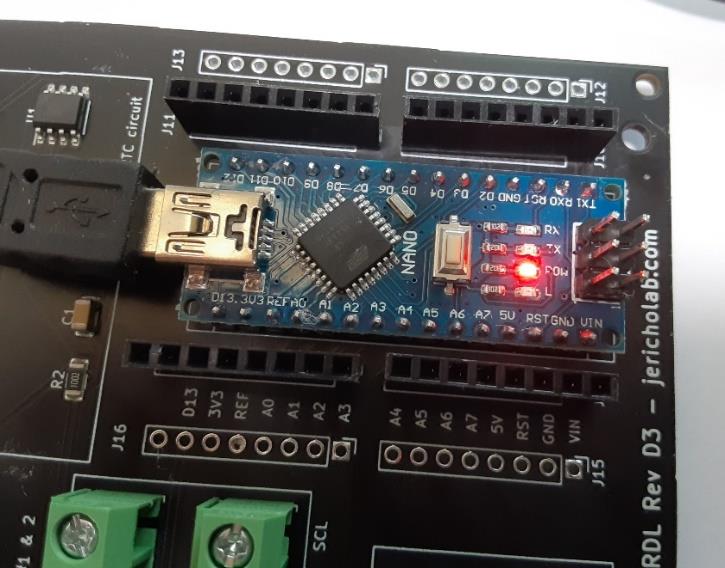
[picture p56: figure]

Figure 5 USB connection and power red light

4- If this is not already the case, connect each required thermistor to its dedicated channel with the provided screwdriver. For this quick test, three probes are required. Other probes can remain connected without problems. Thermistors have no polarity, so you can invert the two wires without consequence. Make sure that the thermistor ID is coherent with the channel in the source code (see Table 2). Make sure that the terminal contact is solid by pulling slightly on each wire. If using extension wire, the wire gauge should be AWG26 or larger to ensure a solid and easy connection to screw terminals. Smaller gauge can be difficult to use.

Figure 6 Connecting the thermistor probe wires to the dedicated channel C1

Table 2 Example of an 8-probe setup with matching probe ID’s

Channel | Connected Probe ID | Source code Probe ID
C1 | S002 | S002
C2 | S003 | S003
C3 | S004 | S004
C4 | S008 | S008
C5 | S009 | S009
C6 | S010 | S010
C7 | S011 | S011
C8 | S012 | S012

5- Download the latest version of the free Arduino Software IDE for your operating system on the Arduino official website (www.arduino.cc). Follow the instructions provided by the website. We suggest installing the English version to more easily follow the User Guide instructions initially.


Figure 7 Arduino official website software download section

6- Launch the IDE software and modify the configuration settings. Go to Menu -> Tools.
a. Board -> Arduino Nano
b. Processor -> ATMega328P (Old Bootloader)
c. Port -> COM4. The exact port name might vary depending on your system. (e.g., ttyUSB1, ttyUSB2, COM1, etc.) You can disconnect/reconnect the USB cable to see which port name appears when you connect the RDL.

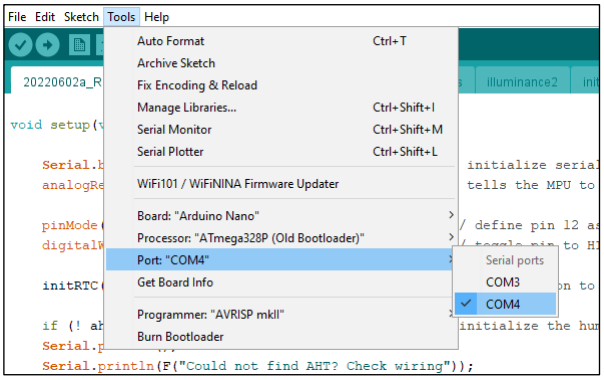
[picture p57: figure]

Figure 8 Serial port selection through the Arduino IDE menu

7- Go to Menu -> Tools -> Serial Monitor. A new window should pop-up. At first, the data being displayed on your screen will be gibberish, because the baud rate (i.e., communication rate) is wrong.

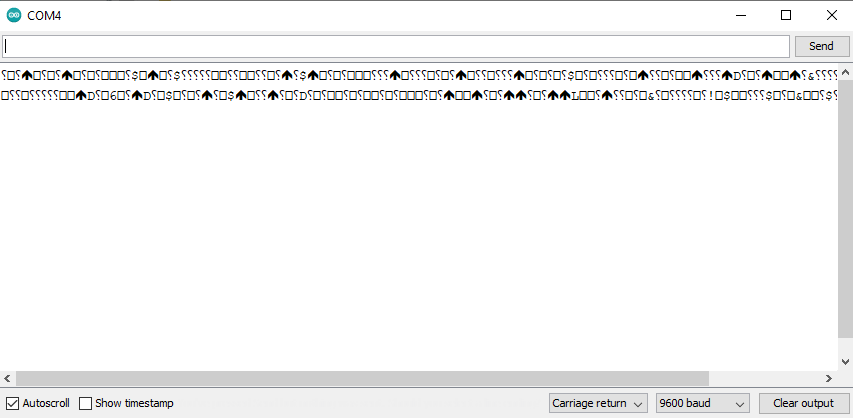
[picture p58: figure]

Figure 9 Example of gibberish data coming in due to a mismatch of the baud rates

8- The baud rate inside the RDL source code should match the baud rate of the computer. On the bottom right of the Serial Monitor window, set the baud rate to 57600 (program default is 9600). Once the baud rate is correct, readable data will start coming in through the Serial Monitor.

Figure 10 Serial Monitor window components. 1) Command line; 2) Send command button; 3) Activate/Deactivate autoscroll; 4) Show/Hide timestamp; 5) Selection of the end of line symbol; 6) Selection of the baud rate; 7) Clear the window.

9- Select the ‘Carriage return’ in the End of line options (item 5 in Figure 10). Otherwise, the command will not be recognized by the RDL.
10- The factory setting for the acquisition rate is 1 Hz (i.e., 1000 milliseconds interval). You can modify it to 2000 ms or leave it at 1000 ms. To modify that value, you must enter the text “INTERVAL” in the command line (item 1 in Figure 10).
11- If there are too many columns, you can zoom out by using CTRL + the mouse wheel. ‘Autoscroll’ can be deactivated to look at the data.


Figure 11 Example of an interval modification from 1 to 1000 ms through the command line

12- Before starting your experiment, you can clear the window by clicking on “Clear output” in the bottom right of the window (item 5 in Figure 10). Otherwise, non-relevant data can be erased later during post-treatment.
13- You can now proceed with your experiment. Meanwhile, using adhesive tape, position the three probes in the following way.
a. Probe C1: Near the liquid exit to measure the temperature of the coffee outflow;
b. Probe C2: Near the bottom of the cup, without touching the bottom surface, if possible. This will allow measuring the global temperature of the coffee accumulated in the cup.
c. Probe C3: In the center of the top surface of the espresso machine. This surface becomes hot during the warm-up and operation phase since the boiler is right beneath the surface. It can be interesting to see how its temperature evolves over time.
14- Prepare the coffee as usual, and turn on the machine to preheat. Wait until the temperatures stabilize on your screen before activating the compressor (brewing phase).


Figure 12 Caption


Figure 13 Position of the two probes inside the empty cup

15- As the experiment unfolds, watch the data accumulate in the Serial Monitor window. Each time, the RDL sends data, the light ‘TX’ on the controller should blink very quickly.
16- When you have gathered all your data, untick the case ‘Autoscroll’. This will prevent the screen from moving while you select your data. Do not close your Serial Monitor window until you have saved your data in another reliable location.
17- Press “CTRL + A” to select all text. Then copy by pressing “CTRL + C”.
18- Open a text editor and paste all text by pressing “CTRL + V”.


Figure 14 RDL text file output sample

19- Save the text file on your Desktop (ex: test_1.txt). This is an important step, since the data within the Serial Monitor is not recorded permanently. Data is lost when the window closes. 20- Open Microsoft Excel or, alternatively, a free spreadsheet software (e.g., LibreOffice Calc).
21- Go to Menu -> Data -> From text. Select the text file. In some recent versions of Microsoft Office, you might have to activate “Legacy Wizards” in order to have access to data import from a text file. If this is your case, follow Microsoft instructions on the topic on their forum.


Figure 15 Microsoft Excel menu for the Text Data Import

22- Select the ‘Delimited’ data type.

23- Select the ‘space’ character as the delimiter. Tick the box ‘Treat consecutive delimiters as one’. Click Finish.

24- Import data to ‘Existing Worksheet’.

25- If necessary, adjust the ‘timestamp’ column cell format to ‘Short Date’ in order to display the time properly.
26- Clean up the data. Over long periods of measurements, a few lines will have a missing character. This happens more frequently with smartphones than computers.

Figure 16 Cleaning up the raw data

27- You can now create various graphs from your data. For example, you might create a “Line graph” with the column ‘Time’ as the x-axis and three temperatures as the y-axis. In our case, we decided to put data from channel C4 on a secondary vertical axis.

Figure 17 Data treatment inside Microsoft Excel


Figure 18 Example of data post-treatment with MS Excel ® for the espresso machine experiment

28- Analyzing the data is the final and most interesting part of the experiment. First, it is good practice to analyze the quality of the data. Are there any surprises, irregularities, noise in the data? Second, what are the trends that we observe in the data (peaks, valleys, plateau, oscillations, etc.)? Here are a few examples for the espresso machine graph.
d. The temperature of the coffee outflow sensor increased very fast initially. Due to the thermal inertia of the large sensor, it is not clear at what time the coffee temperature outflow really peaked. It would be interesting to rerun the experiment with a small probe, which has lower inertia. If the curve does not change, that would suggest that probe inertia does not play a significant role on this specific aspect.
e. Both coffee temperature sensors peaked before the end of the brewing. Since we know that the brewing lasted around 30 seconds, we can confirm that the heater element is not powerful enough to maintain the maximum temperature of the water. The maximum heating power [watts], the coffee grain thermal inertia and the water reservoir temperature are likely to play a role in the curve of the coffee temperature.
f. There seems to be a slight inflexion point around 18:20:06. This could be the time at which the brewing stopped. We could improve our observation by plotting a first order time derivative of the data for C1 and C3. It would be easier to see if our eye is being misled. That could be confirmed with a second experiment which measures the start and stop of the compressor. This could be measured in one of several ways: manually with a clock, with a current sensor, or with a digital switch.
g. The two sensors eventually converged to a very similar temperature. This is likely to indicate that after a few seconds without liquid inflow, the stratification became negligible due to conduction and convection within the cup.
h. There was very little change in the temperature of the top surface (less than a degree). This was a surprising result as one could expect that the incoming cold water from the reservoir would have had some effect on the machine casing temperature. Also, with the help of the secondary axis, we can see that much of the temperature increase happened after the brewing. This challenges our understanding of the espresso machine.
i. The top surface temperature had not peaked when the experiment ended. It would be interesting to run the experiment longer for that reason.

As you can see, much can be learned from a single graph. A first experiment often leads to a series of more refined experiments.
29- We advise you to keep the original data (i.e., text file) in case you eventually want to restart your analysis from scratch for a variety of reasons.

### RDL FACTORY SETTINGS

Factory settings are the settings active when you first receive your device. Most of the RDL capacities are active in order to easily demonstrate every aspect of the product. The factory settings are a combination of memory parameters and source code parameters. You can alter the factory settings by combining serial commands and small source code alterations. You can always go back to factory settings by using the command “EEPROM-ERASE”.

Factory settings (EEPROM section)

- Acquisition interval: 1000 mS
- Number of probes: 16

- Temperature unit: Celsius
- Sensors probes: All 16 resistive channels are defined as temperature sensors. The corresponding 16-character code stored in the microcontroller is “TTTTTTTTTTTTTTTT”.
- Humidity probes: Channel C1 is associated with a dry bulb (A) and Channel C2 is associated with a wet bulb. The corresponding 8-character code stored in the microcontroller is “A1000000”.

Factory settings (source code section)

- Time display: Yes
- ID display: Yes
- Temperature display: Yes
- Resistance display: Yes
- Humidity display (wet bulb based): Yes
- I2C display: Yes
- Voltage reading display: Yes
- Luminosity display: Yes.
- Soil humidity display: Yes
- Wet Bulb Globe Temperature (WBGT) display: Yes
- Steinhart-Hart thermistor coefficients (A,B,C):
- For the Starter Kit package
- Channels C1 to C8: Custom coefficients specific to included thermistor probes
- Channels C9 to C16: Generic coefficients for 10k NTC thermistor
- For the Controller-only package
- Channels C1 to C16: Generic coefficients for 10k NTC thermistor

### AVAILABLE SERIAL COMMANDS

In order to interact with the RDL, the user must type in some of the following keywords at the top of the ‘Serial Monitor’ window and then click ‘Send’. The option ‘Carriage return’ must be selected for the RDL to detect the command. The commands are not case-sensitive.

HELP: The command ‘HELP’ prints out the available serial commands. Activity will resume after a few seconds.
INTERVAL: The command ‘INTERVAL’ allows adjusting the measurement interval (i.e., acquisition rate). The same rate applies to all sensors. After receiving the command, the program will wait for the user to enter a value between 1 and 96 400 000 ms (i.e., 24 h). Enter the value ‘1’ to force maximum speed, which will vary depending on the number of active probes. The default factory value is 1000 ms (1 second).

The maximum acquisition rate depends on a combination of factors:
- amount of sensors/values/data printed per poll
- baudrate (source code default is 57600, but the Nano can reach 115200)

- RTC use (DS3231b performance degrades above 57600)
- speed of the PC/smartphone (buffer overload)

Note: For intervals shorter than 1000 ms, we recommend activating the serial monitor native timestamp, which includes milliseconds. Otherwise, all datapoints taken within the same second will receive the same timestamp from the RTC (hh:mm:ss), which can be problematic for plotting time series afterwards. You can keep the RTC timestamp though, as the native timestamp does not include the date.
CELSIUS: The command ‘CELSIUS’ tells the device to display temperatures in Celsius (°C) units. Unit is stored in the permanent memory (EEPROM) and will be remembered after a shutdown or reset of the device. Celsius is the default factory setting. No confirmation or further instructions are required. Operation will resume after a few seconds.
FAHRENHEIT: Display temperature in Fahrenheit (°F) units. No confirmation or further instructions are required. Operation will resume after a few seconds.
KELVIN: Display temperatures in Kelvin (K) units. No confirmation or further instructions are required. Operation will resume after a few seconds.
COEFF: Print out the Steinhart-Hart coefficients presently stored in the controller memory. No confirmation or further instructions required. Operation will resume after a few seconds. EEPROM-ERASE: Erase the EEPROM memory and return to the factory settings (RATE 1000 ms, Celsius units, all 16 channels active). No confirmation or further instructions required. Operation will resume after a few seconds.
RESET: This command restarts the microcontroller. It is the equivalent of pressing the RESET button on the Arduino Nano. This is convenient to print out the header when starting a clean measurement session for logging purposes. Operation will resume after a few seconds.
SENSORS: This command determines which sensor type is connected to each of the 16 multiplexed channels. After the initial command ‘SENSORS’ is sent, the program expects a 16-character string to be entered (e.g., “TPTPTPTPTTTTTTTT”), where T stands for temperature sensor, P stands for photoresistor. 30 seconds are allowed to enter the data. If no data is received within this delay, the previous value is maintained and operation resumes.
HUMIDITY: Relative humidity is calculated by post-treatment of the sensors data. A dedicated string called humidity informs the microcontroller of which channels are dry bulb temperature sensors and which ones are wet bulb temperatures sensors. 30 seconds are allowed to enter the data. If no data is received within this delay, the previous value is maintained and operation resumes.
Letters (A,B,C...) identify the dry bulb temperature sensors.
Digits (1,2,3...) identify wet bulb temperature sensors.
'0' identify the channels which are not concerned with humidity measurements. The factory setting is ‘A100 0000 0000 0000’’.

Example #1: 'ABCD123400000000 '
This is the maximum number of independent humidity measurements that you can do with one RDL device. Channels C1, C2, C3, C4 are dry bulbs and are matched with wet bulbs from the channels C5,C6, C7, 8 respectfully. Channels 9 to 16 are not concerned with humidity.

Example #2: 'AB00120000000000'
This is an example of two humidity measurements and 12 channels not concerned with humidity measurements (could be surface temperatures or else).

Eample #3: 'A000120000000000'
This is an example of vector that will generate an error due to an unpaired dry bulb channel. The program will therefore keep the previous parameters.

### IMPORTANT USER PARAMETERS

Most variables within the source code should not be modified by the user during normal operations, but some important parameters are not available through the serial commands and need be modified within the source code before uploading it to the microcontroller.

- Generic
- Activate (1) or Deactivate (0) the use of the generic Steinhart-Hart coefficients of thermistors (10 kohm @ 25C, B = 3950). The generic coefficients should be used when uncalibrated thermistors are connected. The generic coefficients should be deactivated when calibrated thermistors are connected to the RDL and the known coefficients have been substituted in the source code.
- Generic = 1 (Active)
- Generic = 0 (Inactive)
- Time display
- Activate (1) or Deactivate (0) the use and display of the Real-Time Clock (RTC). The Real-Time Clock allows the RDL to keep track of the date and time with high accuracy. The RTC clock is polled at every cycle and its data is printed out in the serial monitor. This is especially useful for experiments that last more than 24 hours since most Serial Monitor Data Logging software do not keep track of the date. The RTC poses a restriction however in the maximal speed that the RDL can operate (approximately 5 Hz).
- TimeDisplay = 1 (Active)
- TimeDisplay = 0 (Inactive)
- Identification Number display
- Activate (1) or deactivate (0) the display of the identification number (ID). By default, the source code attributes an identification number to each measurement (i.e., 1, 2, 3, etc.) The ID can supplement or substitute the timestamps in some cases, such as high-speed measurements. It is also useful during post-treatment to keep track of the data continuity (i.e., lines 2450 to 2460 are missing due to bad data)
- idDisplay = 1 (Active)
- idDisplay = 0 (Inactive)

- Temperature/Illuminance display
- Activate (1) or Deactivate (0) the display of the temperature/illuminance value for the multiplexed channels. Deactivating the temperature display can be useful when the user is not using the multiplexed channels or is not using them with thermistors or photoresistors. In that latter case, the user might only activate the display of the resistance values.
- tDisplay=1 (Active)
- tDisplay=0 (Inactive)
- Resistance display
- Activate / deactivate the display of the resistance value for the multiplexed channels. Deactivating the resistance display can be useful in cases where the user is not using the multiplexed channels or is only interested in temperatures.
- ohmDisplay = 1 (Active)
- ohmDisplay = 0 (Inactive)
- Humidity display (wet bulb based)
- Activate/Deactivate the calculations and display of relative humidity based on the dry bulbs and wet bulbs available.
- humDisplay = 1 (Active)
- humDisplay = 0 (Inactive)
- I2C display
- Activate (1) or deactivate (0) the use and display of the I2C sensors connected to the I2C channels of the RDL. The content of this tab can vary. The native source code demonstrates the I2C abilities of the RDL with the AM2301b digital temperature/humidity sensor.
- I2CDisplay = 1 (Active)
- I2CDisplay = 0 (Inactive)
- Voltage display
- Activate/Deactivate the measurement, calculation and display of the voltage input in the corresponding channels (0-5V, continuous current).
- VoltDisplay = 1 (Active)
- VoltDisplay = 0 (Inactive)
- Soil content humidity display
- Activate/Deactivate the calculations and display of the soil content humidity based on the gypsum blocks and the temperature probe available. The gypsum block resistance being sensitive to temperature, they must be corrected.
- SoilDisplay = 1 (Active)
- SoilDisplay = 0 (Inactive)
- WBGT display
- Activate/Deactivate the calculations and display of the Wet Bulb Globe Temperature. The WBGT is calculated from three values: the natural wet bulb temperature, the dry bulb temperature and the black globe temperature.

- WBGTDisplay = 1 (Active)
- WBGTDisplay = 0 (Inactive)

### HOW TO UPLOAD THE SOURCE CODE TO THE RDL

The RDL already comes ready-to-use, but you might want to make some changes to the source code or use the latest release.

1- If this is not already done, do steps 1 to 6 inclusively from the Quick Start section.
2- Download the latest source code on the Jericho website (zip file).
3- Unzip the source code in your working directory. The folder name should be the same as the main file without the file extension (e.g., 20220602a_RDL_main_revD3_stable)
4- Open this code file with the Arduino IDE software. (File -> Open)
5- Make the desired modifications to the code.
6- Insert the Steinhart-Hart coefficients (thermistor) to match your physical hardware into the main tab of the source code. The source code from the website has generic coefficients, which you can comment out using the ‘//’ symbol. You can find the coefficients specific your serial numbers in the Jericho database.

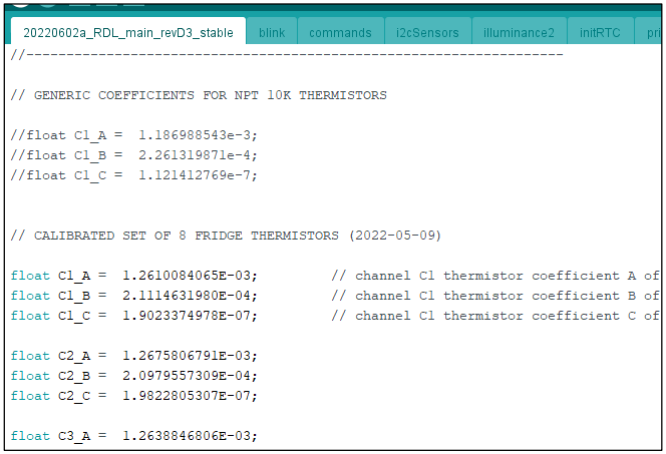
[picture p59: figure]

Figure 19 Custom thermistor coefficients updated in the source code, based on calibration certificate

7- Connect the RDL to the computer via the USB cable.
8- Make sure that the proper USB port is selected by the software.
9- Install all the required libraries. Go to Menu -> Manage Libraries. This is necessary even if you don’t plan on using some of the features (e.g., I2C humidity sensors) due to their presence in the source code, even when the features are not activated. EEPROM.h is included in the source code but is not required to install since it is native to the IDE software.
a. RTClib.h by Adafruit
b. Adafruit_AHTX0 by Adafruit

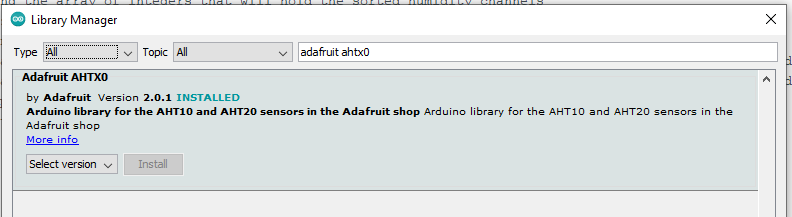
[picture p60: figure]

Figure 20 Searching the Adafruit AHTX0 library within the Arduino IDE Library Manager

10- Go to Menu -> Sketch -> Upload. This will compile then immediately upload the code to the RDL. The “RX” and “TX” LED light should flash quickly while the code is being uploaded. Normal upload time should be 10 seconds. Normal compile time should 10 to 15 seconds. Total time should then be 20 to 25 seconds.
11- Follow the steps from the Quick Start guide to open the Serial Monitor and see if you get the expected results.

For more help about Arduino coding and debugging, visit the official forum on arduino.cc or ask your local community: the Arduino platform is very common worldwide.

### HOW TO LOG DATA TO FILE FOR COMPUTERS (UPCOMING FEATURE)

The Arduino IDE can hold large quantities of data inside the serial monitor window. However, this data is kept in memory temporarily, and eventually the data would have to be copied manually to a text file for permanent storage. There is always a chance that the computer or program would shut down before doing that operation. It is therefore best to save data as we go to a text file. There are a few different ways to log the data, depending on your setup and skills.

The ‘logging script’ can be used.

1- Download the latest ‘logging script’ from the Jericho website. 2- Open a new Terminal window.
3- Go to the script folder.
4- Launch the script.
5- After a few seconds of data logging, open the text file to make sure that data is being saved on a continuous basis.
6- (Optional) Launch the gnuplot script in a second window for a live visualization of the data.

### HOW TO USE THE RDL WITH A COMPUTER

While the Arduino IDE can be used for logging with some projects, here is an overview of the different ways of using the RDL with a computer.

Important: Whatever the method chosen, it is important that the computer does not sleep. When going to sleep (e.g., closing the lid) the data logging is interrupted. The USB voltage supply is maintained but the serial communication is interrupted.

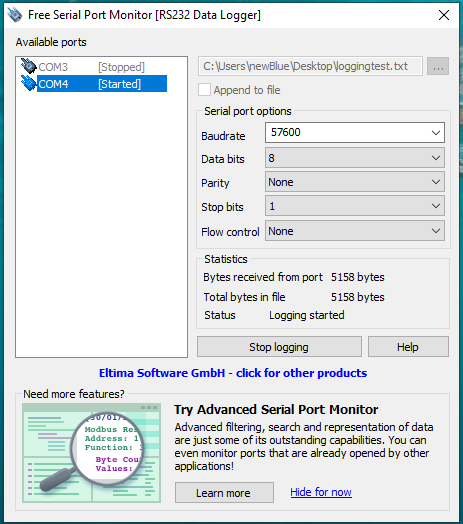
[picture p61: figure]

Figure 21 Example of a free Serial Monitor Program for Windows

Coding (alternatives to the official Arduino IDE)

- Atom (with the PlatformIO add-on)

Data Logging (Windows)

- Jericho Processing script (free, open source, tested)
- Free Serial Port Monitor by Eltima (free, proprietary, tested)
- YAT (Yet Another Terminal) (free, open source, not tested)
- HyperTerminal (paid, proprietary, not tested)

Data Logging (Linux)

- Jericho Processing script (free, open source, tested)
- CuteCom (free, proprietary, only saves to file at closing, which is a data loss risk)

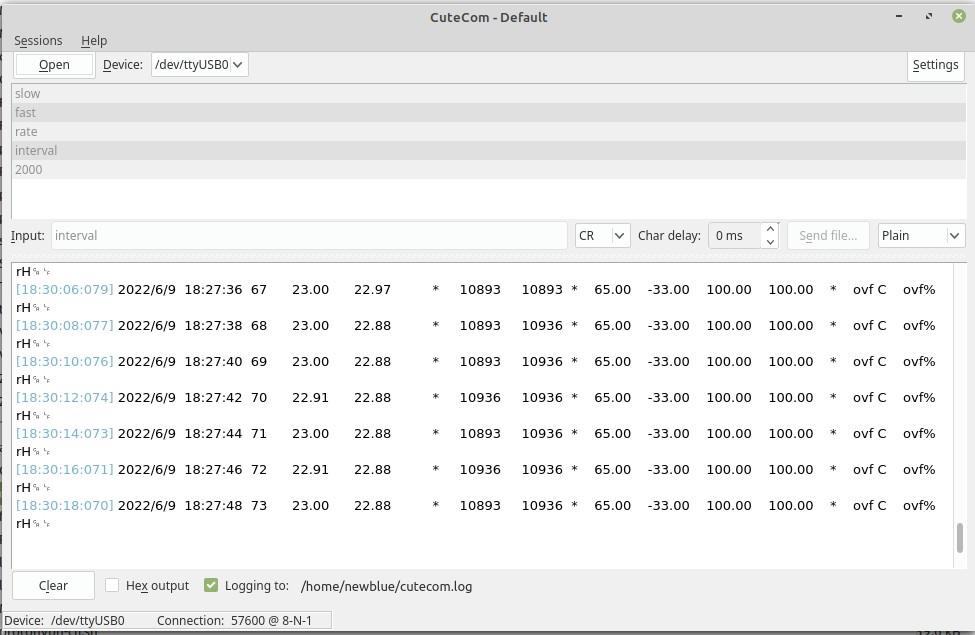
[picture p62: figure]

Figure 22 Screenshot of CuteCom while data logging from the RDL

Data Logging (Apple)

We currently do not support Apple devices. The Processing script should work, some Serial Monitor apps are available (e.g., CuteCom), but we did not do any test with the Apple OS environments.

Live Graph (all OS)

The RDL is not aimed at users with live visualization needs. There are however two methods to do so minimally, and it might satisfy some users needs.

1- Serial Plotter

The official Arduino IDE has a Plot Monitor, which allows to automatically plot the incoming serial data if the data is clean. This requires to deactivate the prints that are not required or compatible. For plotting the thermistor temperature values, you will have to deactivate: ID, RTC timestamp, resistance, humidity, I2C sensors. This will make sure that the program can detect the relevant data (i.e., temperatures) and select a suitable axis range to display it.

Important: it is impossible to save the data while plotting with the Serial Plotter. The Serial Plotter does not keep the data in memory. Even if you try to activate a second program, like CuteCom, it is not possible for two programs to maintain a connection with the microcontroller simultaneously. Therefore, the live graph must be used for debugging purposes, or applications that do not require data logging.

Figure 23 Example of a simple live temperature plot available by combining the RDL and the Serial Plotter feature by Arduino IDE

2- Processing + Gnuplot

There is the possibility of logging the data continuously with a Processing script, and then write a second script (with Gnuplot or Python) that would poll the text file continuously. This would allow the user to visualize live data while logging as well. However, we do not currently support this option.

### HOW TO USE THE RDL WITH A SMARTPHONE

Smartphones can be used to communicate and log the data from the RDL for significant periods of time. There is currently no way to draw live graphs from a smartphone. A free third-party Android apps exists, ArduinoDroid by Anton Smirnov, to write, compile and upload code to the Arduino-compatible microcontroller, but it currently has limited features and reliability.

To use the RDL controller with a smartphone, you will need:

- RDL controller;
- Computer with internet access (for the initial configuration of the RDL and the post-treatment)
- On-The-Go hub such as the SUMAYA, with the good USB type (around $C15 on Amazon);
- Serial Terminal Android app, such as SERIAL USB TERMINAL, by Kai-Moriche (free, available on PlayStore)
- Cloud account, such as Dropbox (free up to 10 GB);
- Cloud Android client, such as Dropsync by MetaCtrl
- free up to 10MB files, $C9 for unlimited size
- use the one-way sync mode (upload only) to avoid file writing conflicts
- Wifi access or a dedicated smartphone data plan

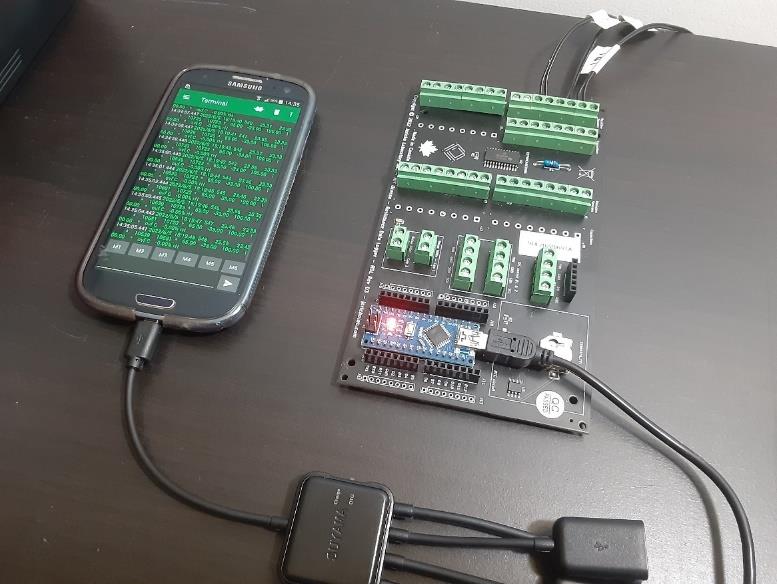
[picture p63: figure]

Figure 24 Samsung S3 logging from the RDL rev D3 through an OTG hub

Jericho does not sell the accessories required for smartphone operation (i.e., OTG cable, OTG hub). We do not recommend USB adapters, since the ones we tested have proved to be unreliable (e.g., intermittent contacts). Hubs have shown to be of better physical constructions and reliability. While shopping, be careful to avoid “charging-only’ cables. These cables have four pins instead of five, and will not allowing communication.

In the field, it is better to not use a computer. Because you want to have a more compact system and avoid leaving a high-cost computer in the field. The solution is to use a smartphone. The smartphone role is to provide energy, data storage and communication. Smartphone mode operation can also be useful to reduce cost, since an early-generation smartphone can be cheaper than a desktop or laptop computer.

Smartphone also allow the use of the cellular network (e.g., LTE), without the use of any additional component. It can simply upload the data through the cellular network. This allows the monitoring of stuff in remote locations such as forests, agricultural fields without the need to go pick up the data on a regular basis. The live transmission of data also reduces the length of missing data in case of problem, since the dysfunction of the apparatus would show up instantly in the bad or missing data. It also allows using the inner sensors of the smartphone.

Important: Most USB OTG hub have a CHARGE mode and an OTG. To be able to charge the smartphone while logging, you must position the hub to CHARGE mode.

Smartphone inner sensors

It is not very common knowledge that smartphones sensors raw values can be accessed and logged. There are a few free applications that allow to do that. Some common smartphone sensors include:

- Geolocation (Latitude, Longitude, Altitude);
- Accelerometer/Gravity;
- Velocity;
- Orientation;
- Proximity;
- Luminosity;
- Electromagnetic field;
- Battery temperature and charge;
- Sound level.

The accuracy of those sensors will vary for each smartphone, but the specifications are available through the manufacturer. These internal sensors can be a good complement to the RDL sensors. For example, it might be extremely useful to combine GPS data with temperature, if you are monitoring the temperature of car component as you drive.

In practice, you will get one text file for the RDL and one text file for the inner sensors, because these are produced by two different apps. Both files are then synchronized to your Cloud. They can later be merged into a single spreadsheet.

There are some limitations, however. First, the timestamps will not be synchronized, which will cause some discrepancy when you merge the datasets. Second, this will increase the smartphone power consumption.

Android app example: “AndroSensor” by Androsensor
Apple app example: “Physics Toolbox Sensor Suite” by Christian Vieyra.

Not all apps can log the data they display (e.g., Sensors Multitool” by weRed Software). Not all sensors can be logged by all apps. For example, Sensors Multitool is unable to log battery temperature (bug).

Specific notes about the Serial Terminal App 1.44 by Kai-Moriche

We recommend using at least 50 kB buffer (Settings in the App Menu). A smaller buffer will cause some issues (i.e., overflow, lag, gibberish symbols, crash) especially when a larger number of sensors are active.

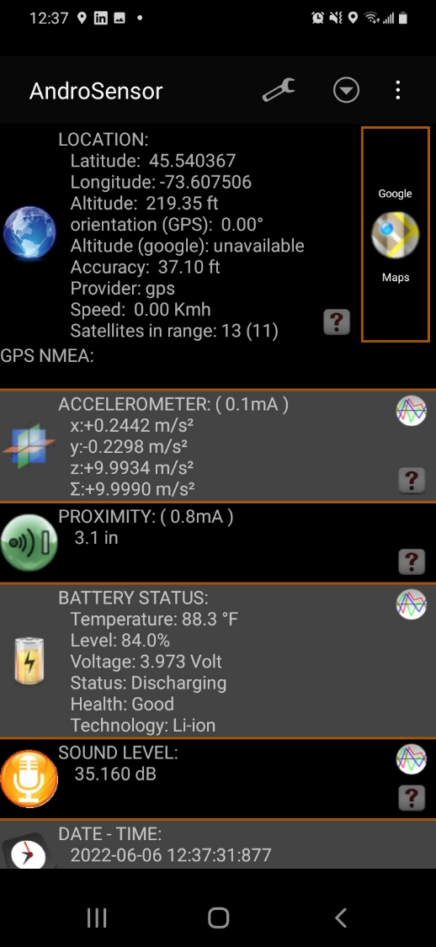
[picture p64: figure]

Figure 25 Screenshot sample of the AndroSensor app for Android Samsung A10 (not all sensors are visible)

Choosing a smartphone

For RDL operation, we recommend the use of Android smartphones. Apple products could also be used, although we have not made any test. The old Samsung S3 (2013) has proven to be a suitable candidate for smartphone operation. It has been sold in 40 million copies worldwide, hence it is available for cheap on the second-hand market (C$75), and it has a higher number of inner sensors than more recent phones. One downside is that it is not officially supported any more by Android, and so the security, support and compatibility levels are decreasing day by day. Original batteries have usually expired by now, but replacement batteries from third-parties are available on e-commerce website for around C$15. The battery can be installed in a few minutes, since batteries were not glued back in earlier smartphone designs.

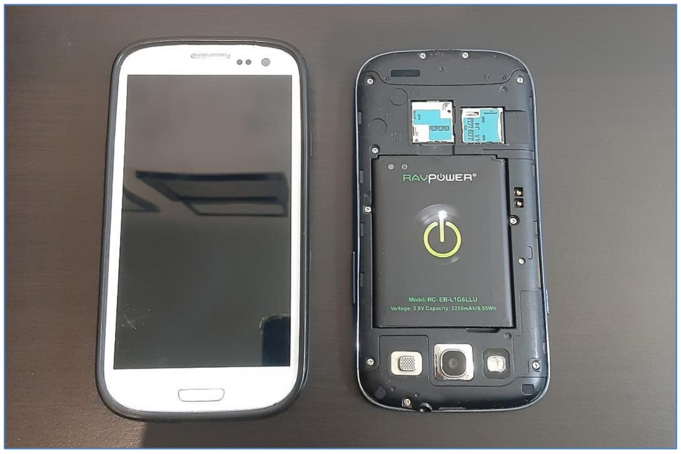
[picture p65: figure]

Figure 26 Two units of the Samsung S4 smartphone, with a replacement battery

This is a great way to reuse electronics that are otherwise mostly obsolete. Users with a higher budget can use entry-level brand-new phones, such as the Samsung A10 or A03S (approximately $C200). When choosing a smartphone, you should try to select one with minimal power usage. Older smartphones are usually less power hungry nominally. More recent smartphones are usually more power hungry, due to ever increasing performance and larger screens. However, recent smartphone also benefits from more efficient low-power modes. This will increase the duration of the system power supply (internal or external) and reduce the size of the required solar panel, if applicable.

If you are unsure about your smartphone OTG abilities, apps such as “USB OTG Checker” can be used to verify that a phone is compatible with OTG communication. The recent Note 7 smartphone from Chinese manufacture Cubot, for example, does not have OTG abilities.

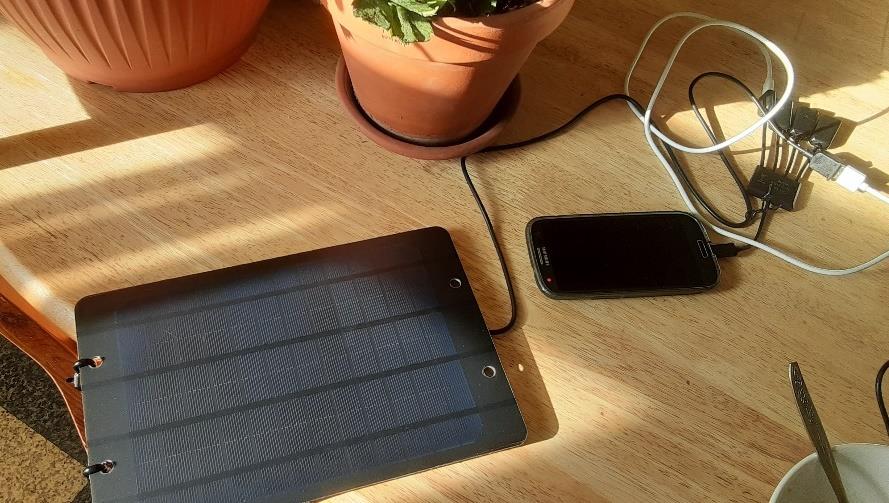
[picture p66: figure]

Figure 27 Example of a 5V-regulated USB solar panel connected to a RDL-smartphone setup

Power

The smartphone has a USB connection - usually type micro or mini. Therefore, they can provide a regulated 5V signal just like computers. When a smartphone is connected to a computer, it usually becomes a SLAVE to the computer HOST. This means that the computer leads the communication. However, an increasing number of smartphone models are able to act as a host. This allows smartphones to use a mouse and keyboard, for example. Detailed documentation is widely available on the internet to describe the variants of the SLAVE-HOST paradigm.

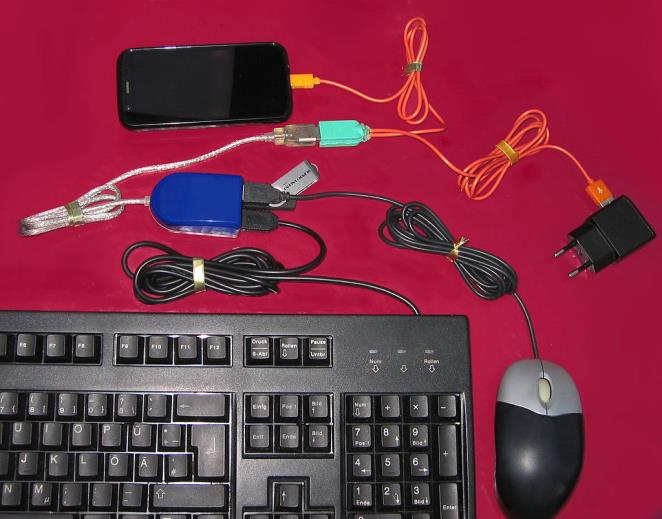
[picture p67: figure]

Figure 28 Example of OTG use
(Photo by Hans Haase - Own work, CC BY-SA 4.0, https://commons.wikimedia.org/w/index.php?curid=40618659)

Hubs are a variant of the OTG cables. OTG hubs usually have two-modes of operation: CHARGE and ON-THE-GO. The Charge mode is intended to charge the phone with the hub. The On-The-Go mode is intended to communicate with the USB device (e.g., mouse). In that mode, the phone is not being charged. A reduced set of phones have what is called a SIMULTANEOUS mode. The Samsung S3 is one of those. It means that when the hub is in CHARGE mode, the phone is still able to communicate. This is the most desirable mode of operation, since it allows indefinite operation of the RDL.

USB hubs are usually limited to 2 amps or less, so be careful not to use them with charging blocks that can deliver more 2 amps. Failure to respect the manufacturers indication on that regard can result in equipment melt-down and fire hazard. Always verify the specifications of the charger before using it with a USB hub.

Figure 29 Example of a compatible OTG hub sold by TUSITA

It is important to note that in this simultaneous mode, the smartphone does not supply energy to the slave. The power must come from the hub. This means that a constant supply of energy must be provided in order to create a continuous measurement. This proscribes the use of solar-panel-only systems. It requires either a charger wall adapter, a large battery or a solar-panel-battery system (Figure 2).

Data Storage

Data storage is an important consideration in the design and operation of any data logger system. An independent storage (i.e., internal for the RDL) increases the complexity and cost of the system. Jericho’s choice of smartphone reduces the complexity and cost of the RDL, as well as having important synergies with the communication aspect (next section). Internal data storage of the 2012 Samsung S3 is 8 GB, which far exceeds the needs of most data logging activities.

Communication

Communication between the RDL and the smartphone is done through serial communication, a standard established for decades.

There are a few ways to retrieve the data:

- USB upload: It is possible to just get the data at the end of the experiment. That means recovering the system and connecting to a computer. You can then access the internal memory of the phone and copy your data files to your computer. The user needs to know the folder path. The folder path is usually indicated within the options of the serial monitor app.
- Manual email: It is possible to occasionally reach your system, and send the data file by email. The user needs to know the folder path. The folder path is usually indicated within the options of the serial monitor app.
- Cloud sync: You must subscribe to a Cloud service, then find a client app for your phone. This can be a problem for very old phones like the Samsung S3. The client needs not only to allow connecting to your account, but ideally, to automatically sync. This can be problematic for some services. For example, Google Drive official Android client does not support Android 4 anymore. This means you won’t be able to download it from the Play Store.
- For Dropbox, there is a functioning client but it does not have the auto sync function. This is why, a third-party, such as Dropsync is needed. Dropsync requires Android 5.0 (Samsung S4) and is free to use under 10MB files. However, if using a large number of sensors or a high measurement frequency, the data size can be significant. Data logging apps like Kai-Moriche do not split the file daily. This means that the file will grow indefinitely (>100MB). This causes two problems. One, the file will stop uploading after it reaches 10MB. This can be solved by buying the full license, which cost C16$ and has no size limit. Second, with the one-file strategy, you will keep re-uploading the complete data set. This is not a huge problem if you are using Wi-Fi, but it will be problematic when using the cellular network, as it might require you to buy a larger data plan. An example of minimal service plan available in Canada is Lucky Mobile. You can buy a SIM card for around $C10 and a 500 Mb data plan for $C15. This is a prepaid plan, that requires no contract and the data is valid for one month. You can replenish as needed. Other companies offer similar plans. It can be more affordable in other parts of the world, such as Europe or India. The overall cost of a fully remote system is presently estimated to be under $C500.

Contrarily to computers, it is not possible at this stage to control more than one RDL device per smartphone. This is because the Serial Monitor apps are designed to talk to one serial device at a time, and Android does not allow opening two instances of the same app.

### RTC TIMESTAMP ADJUSTMENT

To precisely synchronize your Real-Time-Clock (RTC) timestamp with the official time, execute the following procedure:

1. Make sure that your computer clock is synchronized with the official time of your area.
2. Remove the battery in the battery holder (if any).
3. Compile and upload the main code to the RDL by using the UPLOAD button in the Arduino IDE interface.
4. Put in the battery immediately after the upload has finished (see the message at the bottom of the IDE screen).
5. Push the reset button immediately.
6. Time will be set. You might see a warning message if your serial monitor was already opened.
7. Timestamp error is small (20 seconds or less) due to the delay between the start of the compile time and the pressing of the reset button.

After that, any reset or upload will not affect the RTC timestamp until the battery is removed or dies (several years).

Make sure that the code is actually recompiled at the time of uploading, so that the code contains the current time, and note the time registered at the previous compile. To make sure of that, restart the Arduino IDE and change a line of code with a trivial change (like deactivating/activating sensors).

### NOISE CONTROL

Electromagnetic (EM) noise control is an important part of signal measurements. The amount of noise present depends on several factors among which the prevalence of EM noise in the environment and the length of the sensor lead wire. Long lead wires – several meters - tend to act as an antenna and are likely to pick up strong EM noise even in low noise environment such as a residence.


Figure 30 RDL Measurement example, with (left) and without (right) RC filter noise control

The RDL has two distinct mechanisms by which it lowers the prevalence of EM noise. Both mechanisms are optional, independent from one another and can be combined.

1) RC filters
A low-pass filter of type Resistor-Capacitor is present in the circuit.
a. One RC filter is available for each of the 16 resistance channels. This allows individual filtering. The capacitor type and value can be individualized. It is connected to a screw terminal in parallel with the sensor. It is not necessary to add a distinct resistor, as the resistive sensor acts provides the resistance. The filter is optional and can be left empty, when EM noise is not a concern. As an example, for a lead wire of 10 meters, Jericho has had good results with a capacitor of 0.1 uF.
b. One global RC filter is available at the analog input. This allows to filter all channels with a single filter. The use of this filter is indicated when all filters need the same amount of filtering. Two screw terminals are available. This allows the user to combine two capacitors to obtain the desired performance. The filter is also optional and can be left empty, when EM noise is not a concern.

With both techniques, a reading delay (e.g. 100 ms) might have to be implemented. Since the multiplexer only polls each channel for a limited amount time, the condensator needs time to equilibrate each time. Without an RC filter, the multiplexer can poll each channel for a minimal amount of time (i.e. 15 ms), but with an RC filter, some time is needed for the condensator to reach equilibrium. Without a proper delay (e.g. 100 ms) which varies for each case, the ADC might read a lower voltage value than without the RC filter, a significant source of error.

2) Data averaging
Noise filter can also be treated numerically by averaging numerous sample (e.g., 10 samples) for each channel. This is simpler to implement than physical filtering: it consists of modifying the value for the parameter ‘NUMSAMPLES’ in the source code. For maximum speed, use value of 1. For heavy filtering, you can use values of 5 to 20. Since the ADC takes 15 ms per reading, a value of 20 would delay by at least 300 ms per channel. For 16 channels, that would mean a delay of 4800 ms, without accounting for the processing time (i.e., arithmetic averaging). This would limit your ability to gather data at a faster interval than 5s.

### DIGITAL SENSORS

The RDL is able to communicate with digital sensors who use the I2C protocol. Since all sensors use the same data line, each sensor must use a different I2C address. This implies that two units of the same sensors cannot be used simultaneously, as they will both “talk” at the same time. You should also verify that each added sensor does not have an address that is already used. For example, the I2C address of a DS1307 RTC clock is 0x68. This address cannot be used by the sensors. The AM2301b temperature and humidity sensor has the 0x38 address.

### HOW TO RECALIBRATE YOUR THERMISTORS (UPCOMING)

Section to be written in the near future.

### HOW TO USE THE PRODUCT ENCLOSURE

The RDL Starter Kit is provided with a basic enclosure. The enclosure consists of a plastic food container with a snap lid (see figure below).


There is some stigma around the use of plastic food containers as PCB enclosures, as it can appear as “non-professional”. However, this type of item is a great choice for several reasons:

1) Weatherproof, due to its intended purpose to contain liquid food.
2) Extremely affordable component (~$3-4), which helps keep our product price low;
3) Can be substituted by another similar food container if it breaks;
4) Daily tested by thousands of people;
5) Large enough to contain the whole RDL system;
6) Does not conduct electricity;
7) Temperature resistant (freeze, hot liquids)
8) Lightweight (which reduces shipping cost and carbon footprint);
9) Transparent (useful for some sensors or seeing the power ON light) but can be painted.
10) Can be drilled easily to install the PCB standoffs and cable gland(s);
11) Meets the mechanical requirements of most applications;
12) Recyclable (polypropylene (PP) food containers usually have the recycle logo)

Cable gland

To reduce cost, a single cable gland is used for all the wires that must go through the enclosure. This is a non-conventional use of cable glands, as they are usually intended for a single cable and provide a very tight seal. To reduce the infiltration of dust, humidity, insects, etc. inside the enclosure, a little piece of foam can be used to seal the space around the wires. It is also recommended to position the cable gland downwards, when possible, as this will reduce the inflow of water or rain into the enclosure. In applications requiring a better waterproofness, a small amount of urethane can be applied to seal the exit. This will however make it permanent and can be difficult to remove/clean.

Desiccant

To reduce and stabilize the humidity level inside the enclosure, always include a desiccant bag (silicone gel) inside the enclosure for field use. This reduces the likelihood of water condensation on the PCB, which can cause misreading and malfunctions.

PCB standoff screws

Four 3.5 mm nylon standoff screws are used to hold the PCB to the enclosure lid. These plastic screws have low mechanical properties and should be tightened lightly to avoid breaking them. The nylon screws could be replaced by stainless screws if needed. The PCB screws also constitute a possible entry for water. Thin rubber gasket or silicone could be applied to improve the impermeability. Positioning the enclosure with the lid facing down is another way to reduce susceptibility to rain entry.

Outdoor use

The use of the RDL outdoors often requires a weatherproof enclosure to protect the RDL and the smartphone from the elements. Obviously, the food container has no official water-resistant certification like NEMA-3 or IP6, but it aims to be weatherproof. We stress-test this enclosure in a regular dishwasher. In regular cycles (60°C, 60 minutes), less than 30 mL should enter the bottom of the enclosure. Insulation can be added inside the enclosure to help tolerate extreme temperatures (e.g., cold depleted smartphone battery when logging in the winter).

### OPEN-SOURCE LICENSES

Jericho Laboratory operates the RDL product with the following open-source licenses: SOFTWARE: GPL 2.0
HARDWARE: MIT
WEBSITE, DOCUMENTS: Creative Commons CC-BY-NC-SA (Non-commercial use only)

For more information about the user permissions and responsibilities associated with each license, please refer to our website or contact us via email at info@jericholab.com.

### WARRANTY

Our manufacturer warranty includes a 60-day full refund excluding shipping cost. We also provide a 1-year limited warranty on defects. Any misuse, physical damage or modification of the device by the user will void the warranty. This includes but is not limited to: adding or removing components, soldering, bending, cutting, sanding, painting. Made In Canada with International Components.

### CONTACT

For more information, tutorials, FAQ, software updates, accessories and replacement parts, please visit us at jericholab.com. We also appreciate you leaving comments and suggestions.

### ABOUT JERICHO LAB

Jericho is a company based in Montreal, Canada. Our mission is to improve access to scientific equipment by providing provide low-cost high-quality products to students, scientists and engineers. The Rose of Jericho (Anastatica hierochuntica) is a desert plant that can survive years of complete desiccation (absence of water).

### ABOUT ARDUINO

The RDL is compatible with the Arduino language, which is based on the ‘Processing 3’ language, which itself is similar to the C language. Most of the C/C++ core language can be used with the RDL device and the Arduino IDE software. You can create classes, use inheritance, composition, and other functionalities, but STL and exceptions cannot be used. Arduino first appeared around 2005 and is now used worldwide by over a million users. Jericho is not endorsed or linked in any sense with the Arduino company. Arduino clones are produced by hundreds of manufacturers around the world, with different qualities.

Please do not throw away this product to garbage or recycle bin as it can contain toxic substances and/or heavy metals. Please send your Jericho product to your local electronic waste drop-off site so that it can be disposed of properly.

### FREQUENTLY ASKED QUESTIONS (FAQ)

- What is a thermistor?
A thermistor is a tiny passive device which has an electrical resistance that varies with the temperature of its material. It is a word play with the words ‘thermal’ and ‘resistor’.
- Why do I have to connect the thermistor to a specific channel?
Each thermistor has unique parameters called Steinhart-Hart coefficients. Each channel is associated with a specific set of coefficients. Therefore, switching the thermistors would provide inaccurate temperature readings.
- Can I use the RDL to do something else?
Yes, you can modify the product, software and hardware to add or remove capabilities. However, any physical modification of the device will void the warranty.
- I dropped the RDL in the water, what should I do?
Water will create short-circuits that will render the device unusable temporarily. Put it in dry uncooked rice with closed container for 24 to 48h to remove humidity, like you would do for a smartphone. It should work again.
- What other software than Arduino Software can I use to control the RDL device?
The IDE software provided by Arduino is specifically designed for Arduino and Arduino-compatible devices and provides an easy interface to beginners and advanced users. However, some users might prefer to use more professional programming tools. A free option that is often recommended is the software Atom, combined with the Platformio add-on.
- I broke some component. How do I find replacement parts?
You can consult the Bill of Material (BOM) to find the exact part number and order a new part online. If you believe this is due to a manufacturing defect and you are still covered by your warranty, contact us by email.
- Should I tin the wire endings to be used with screw terminals?
No, NASA procedures for example require to NOT thin the wires due to different thermal expansion coefficients of the wire and solder.

### TROUBLESHOOTING

- Error: “An error occurred while uploading the sketch. (avrdude: stk500_getsync() attempt 10 of 10: not in sync: resp=0x31)
- This can happen when the RDL was busy sending sensor data when the PC tried to communicate.
- Try reuploading the program.
- Try disconnecting the USB cable and reconnecting, then reuploading.
- Try another USB port of the PC.
- Try to restart the program.
- Error: “Board at COM4 is unavailable.”
- The selected serial port is not detecting the RDL/Arduino.
- Verify that the USB cable is connected to both the PC and the RDL.
- Verify that the corresponding port is selected in the Arduino menu.
- The printed output of a channel makes no sense. Example, the temperature of the channel C2 is -273.15°C.
- Negative, random-looking values are usually associated with empty or opened channels (false contact, broken probe). Verify that there really is a sensor connected to the channel and that the connection is solid.
- Verify that the channel is properly set up. If the channel is set up as a photoresistor (P) but that physically the sensor is a thermistor, the calculated value will make no physical sense.
- Error: “Variable X was not declared in this scope”
- Two very common reasons for this error is 1) a function was indeed declared at the wrong place 2) a missing bracket or semi-colon has created a complete fuckup of the entire code. It can be hard to find the exact spot. Undo the latest change or go back to your previous working saved version.

### REFERENCES

Arduino Uno Rev3, Digikey, https://media.digikey.com/pdf/Data%20Sheets/Arduino%20PDFs/A000066_Web.pdf

ATmega 328p datasheet: http://ww1.microchip.com/downloads/en/DeviceDoc/Atmel-7810-Automotive-Microcontrollers-ATmega328P_Datasheet.pdf (http://ww1.microchip.com/downloads/en/DeviceDoc/Atmel-7810-Automotive-Microcontrollers-ATmega328P_Datasheet.pdf)

Processing language official website, Processing.org

Free Arduino tutorials, https://www.tutorialspoint.com/arduino/

Yunus A. Çengel. 2007. Heat & Mass Transfer: A Practical Approach. McGraw-Hill Education (India) Pvt Limited.

Learn: Basic knowledge about principles and techniques behind the Arduino ecosystem. https://docs.arduino.cc/learn

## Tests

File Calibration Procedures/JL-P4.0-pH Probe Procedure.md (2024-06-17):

JL- P4.0 - pH Probe Calibration Procedure
=============================
Copyright: Jericho Laboratory Inc.  
Document license: CC-BY-NC-SA

**WARNING**: Jericho Laboratory is not responsible for any damage or your safety if you attempt to reproduce this procedure or any other procedure shared by Jericho Laboratory.

**WARNING**: Be careful when manipulating acids and bases. Wear proper protection equipment according to your legislation.

**Table of Contents**

1. [Introduction](#introduction)
2. [Required Material](#required-material)
3. [Introduction to Buffer Solutions](#introduction-to-buffer-solutions)
4. [Procedure](#procedure)
5. [Notes](#notes)
6. [Useful Commands Summary Table](#useful-commands-summary-table)
7. [Others](#others)
8. [References](#references)

**Introduction**
- This is a 3-point calibration. pH meter are quite linear but not perfectly so, hence a 3-point calibration is required (3 reference solutions).
- The procedure is compatible with the Atlas Industrial Probe Gen3 and Jericho pH meter (which incorporates pH-EZO PCB).
- Atlas Scientific provide their own calibration procedure and documentation. This procedure is complementary to theirs. The user is encouraged to read the Atlas procedure which is found in their specification sheet [1].
- The EZO-PH device is ISO 10523 complient (determination of pH) [2]. The Jericho carrier is not certified.
- The EZO-PH is patented, while the Jericho carrier is open-source.
- The calibration results are stored on the EZO-PH internal memory. The procedure requires access to a computer.
- The calibration is specific to each probe. Since the calibration parameters are internally stored in a closed source code, the calibration has to be done with the final pair to be deployed on site.
- The EZO-PH can operate in two modes of communication: UART or I2C. When you receive the material from Jericho, it is already in I2C mode. However, if you buy an EZO-PH directly from Atlas, it will be into UART mode by default. The UART mode has a green light, while the I2C mode has a blue light on.
- Despite using the probe for soil measurements, you can only calibrate the probe with solutions.
- Another related procedure is the drift test. See section below. A drift test with tap water is the most severe drift test.
- The recalibration interval depends on several factors, such as:
  1. Probe quality
  2. Total Dissolved Solids (TDS) in the solution
  3. Accumulation of debris and organic matter on the membrane surface

**Required material**
- pH probe, uncalibrated, any brand
    - Used: Atlas pH meter probe, Industrial Gen 2 or 3
- EZO PH by Atlas Scientific
- pH carrier board revA1
- RDL revE4
- CAT cable (1-2m)
- 4 beakers or mixing vessels with at least 300mL capacity
- Solutions powder kit (low, medium, high)
    - low value: 4.01 (close to lemon)
    - medium value: 6.86 (close to water)
    - high value: 9.18 (close to baking soda)
- 2L of distilled water or deiodized water
- Protection equipment (gloves, eyewear, clothing)
- Computer with Arduino IDE installed and internet access
- Specialized Arduino program (I2C Example)

**Introduction to buffer solutions**  

- A buffer solution is a water-based solution which has a capacity to maintain its nominal pH value, despite the addition of small quantities of acid or base.
- A buffer solution can be pre-mixed or made from powder+water.
- This procedure uses powders instead of pre-mixed solutions for a few reasons:  
  1. more affordable
  2. easier to store and transport
  3. the accuracy of liquid, pre-mixed solutions is excessive compared with the target accuracy of the system
- While there are various online sellers of buffer powders, the products are often the same. It is not recommended to buy buffer products with too many decimals.
- An example of high-quality buffer solution is Omega calibration solution. It has an accuracy of +/-0.01 pH [1]. Low-cost online venders on Amazon claim the same accuracy but this is untested by Jericho Lab. To play safe, we consider the accuracy of these products to be no better than +/- 0.05 pH.
- The shelf life of buffer solutions varies.
- Storage methods vary depending on format (powder vs liquid). Well, do not freeze and do not expose to sun.
- Note that accurate pH meter measurements and calibrations are known to be difficult.
- The shelf life of pre-mixed solution varies but is usually around 3 years.
- The cost is about $1 per pouch ($3 per kit).

<figure>
<p align="center">
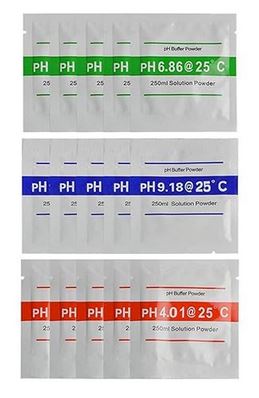
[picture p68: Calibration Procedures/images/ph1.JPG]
  
</figure>
<p align="center">Example of a pH buffer solution powder kit sold on online platforms

**Calibration Procedure**

Day 1

1. Wash all the equipment (i.e. vessel, lid, trays, rod, apparatus, and probes) with soapy water and rinse three times with tap water, then rinse one time with distilled water.
2. Properly identify each buffer solution with a label. Also identify the rinse pot.
3. Pour 250 mL of distilled water in each beaker.
4. Empty the content of each pouch (3) into a beaker. Note that the quantity of powder in each beaker varies.
5. Mix each beaker until most of the powder is dissolved. 
6. Cover the beakers and let rest overnight. The solutions must be used within 24h. The solutions can be kept accurate for some time, but not too long.

Day 2

7. The three solutions should be at room temperature. Measure the temperature of the solutions. Look at the temperature table provided with the buffer solutions to determine the exact pH of the solution.
7.  Connect all the uncalibrated probes to the data logger and activate your RDL data logger. 
8. Load the specialized program onto the RDL.
9. The program will start reading once per second.
9. Let the reading stabilize. Do not exceed one hour when letting the probe adjust to buffer solution.

10. Once the reading is stable, enter the command to modify the reference point in the EZO-pH memory. For example, if you were using the 9.18 pH solution, enter into the serial terminal "'Cal, High'" and follow instructions.
11. Clean the probe in distilled water between each buffer solution.
12. Repeat the other two buffer solutions.
12. To demonstrate repeatability, you should do the calibration twice. The second result should fall within +/- 0.1pH of the target value.

**Notes**
- The measurement accuracy outside the buffer solutions values range is unknown. If you are interested in extreme values (i.e. below 4 and above 10), you will need different buffer solutions.
- Tap water cannot be used for calibrations since the impurities can interac with the buffer chemicals.
- Tap water cannot be used instead of the neutral buffer (7.01) since it has no buffer capabilities. Therefore, any contamination from the previous buffer (a trace left on the probe after rinse) will affect significantly the reading.
- The time required for the probe to reach equilibrium will vary according to the probe (some probes have a less porous membrane) and the ionic strength of a given buffer solution. A less porous membrane may slow down the diffusion of ions into the electrode, thereby extending the time needed to stabilize the reading.
- It takes practice to master the skill of calibration.

**Useful commands sommary table**

- 'R'
- 'Cal, High'
- 'Cal, Low'  
- 'Cal, Med'  

**Others**  

If you have doubts on the accuracy of the reference powders, high-quality pre-mixed solutions can be purchases from Atlas Scientific.

**Reference**   

[1] Atlas Scientific EZO PH Specsheet, pdf. https://files.atlas-scientific.com/pH_EZO_Datasheet.pdf

[2] Pre-mixed pH Calibration Solutions, Omega, https://mx.omega.com/pptst_eng/PHA4_7_10.html

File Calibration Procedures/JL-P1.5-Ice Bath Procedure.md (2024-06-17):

JL- P1.5 - Ice Bath Procedure
=============================
by Jericho Lab
Copyright: 
Document license:

**WARNING**: Jericho Laboratory is not responsible for any damage or your safety if you attempt to reproduce this procedure or any other procedure shared by Jericho Laboratory. DO NOT move a vessel filled with fluid.

**Table of Contents**

1. [Introduction](#introduction)
2. [Required Material](#required-material)
3. [Possibly Required](#possibly-required)
4. [Procedure](#procedure)
5. [Comments](#comments)
6. [References](#references)
7. [Images](#images)

**Introduction**

The ice bath is the most commonly used fixed point temperature. This procedure will typically produce a reference point of 0.00°C +/- 0.01°C (95% confidence interval) at 101 325 Pa \[**NIST reference here**\]. This procedure is part of our three-point calibration. It can be replicated by the user to verify the calibration. In order to let the ice solidify and the water cool, this procedure usually takes two days.

The procedure makes use of a 3D printed accessory designed by Jericho Lab, called the **probe holder**. The design is freely available on our Github repository. The accessory can also be purchased from us. The accessory provides a solid and symmetric positionning of up to 16 probes. It is designed to respect the NIST guidelines regarding the minimal distances between the probe and the vessel surfaces. This makes sure that the probe is really exposed to the ice point. Through its mass, the accessory also provides some thermal inertia, hence reducing the fluctuations of the temperature readings during the procedure.

**Required material**

- Insulated vessel with an insulated lid, with at least a 300 mm in height and 70 mm in diameter (e.g. beverage cooler)
- Jericho’s probe holder (open-Source 3D printed accessory) (see Figure 3)
- Uncalibrated temperature probe
- Distilled water of purity equivalent or better than ASTM Specification D1193
- 1 kg of very small ice cube with maximum size of 1.5 cm, made with distilled water
- Plastic bottle with a cap (500 mL)
- Plastic rod to stir the ice bath
- Powder-free clean plastic gloves
- Tap water

**Possibly required**

- Freezer (typically -18°C (0°F)) (to produce ice cubes)
- Refrigerator (typically 4°C (39°F)) (to keep the water cold overnight)
- Ice cube tray, with maximum cube size of 1.5cm (see Figure at the end of this document for an example)
- Aluminum foil sheet of 30 cm (if the vessel has no lid).

**Procedure**

Day 1

1. Wash all the equipment (i.e. vessel, lid, trays, rod, apparatus, and probes) with soapy water and rinse three times with tap water, then rinse one time with distilled water.
2. Prepare 500 mL of distilled water chilled to near 0°C in a clean plastic bottle (e.g. refrigerator).
3. Fill the ice cube trays with distilled water, and then put the tray in the freezer.

Day 2

1. Put on the plastic gloves.
2. Connect all the uncalibrated probes to the data logger and activate your RDL data logger. Make sure that the printing of the resistance values is activated. These values will be the basis of the calibration calculations.
3. Position each probe in the probe holder. Weight should be added to the probe holder to avoid floating as the plastic accessory is less dense than water. This can be done with 2-3 bolts tied to the probe holder.
4. Position the probe holder in the bottom of the empty vessel.
5. Gently fill the vessel with ice cubes.
6. Shake vigorously the chilled water for 1 minute to aerate, and then add some of the water to the vessel. Leave 1 to 1.5 inch of space at the top with only ice cubes.
7. Ice cube levels should remain one inch above water level at all times during the experiment. If the level is lower than that, add more ice cubes at the top.
8. Stir slowly the water for one minute with the plastic rod. Make sure to not hit the probe holder.
9. To reduce thermal leaks through the lead wire, we recommend keeping as much lead wire inside the cavity as possible – beneath the insulation layer. This will reduce the influence of the room temperature on the probe.
10. Cover the ice bath with an opaque and thermally insulating cover. If this is not possible, at least aluminum foil.
11. Let the water-ice mixture sit for thirty (30) minutes. This allows the ice and water to reach the thermal equilibrium (i.e. 0°C).
12. Once the values are stable (plateau), record 60 values (electrical resistances \[ohms\]) at an interval of 1 sec. Average those values. See figure at the end of the document an example of data set.

**Comments**

1. According to the NIST, the probe should be at a minimum depth of 20 cm to reduce the amplitude of the thermal leak from the electric wire. The probe must remain at least 5 cm from the bottom and 2 cm from the side walls at all time. See figure below for more details. The probe must sit for one (1) minute before the measurements. This last requirement is easily fulfilled by the procedure since the probes are already in the water during the 30-minutes equilibrium period.
2. A non-insulated vessel gives the same temperature point with less accuracy due to a less homogeneous bath temperature. An insulated vessel also lasts longer (a few hours).
3. Demineralized water can also be used, instead of distilled water.
4. Make sure that no bare metal wire is exposed to water.
5. Do not reuse the gloves for a second experiment.
6. Using city tap water instead of using distilled water will typically give an ice-point of (-0.01°C) to (-0.02°C), depending on the water quality in your area (ASTM-E563-11(2016)). Impurities usually lower the melting point.
7. Slow stirring during measurement increases homogeneity and reduces uncertainty.
8. The effect of barometric pressure on the pure ice point is −74 nK/Pa (−7.5mK/atm). With saturated air in solution, the effect is increased to approximately -0.1 μK/Pa (-10 mK/atm) (ASTM E563-11(2016)). Due to the small magnitude of the effect, the phenomenon is not considered in the procedure.
9. The thermistor must be immersed deeply enough to avoid perturbation of the temperature by radiation or thermal conduction along the electrical wire.
10. Ice coming out of a regular freezer usually has a temperature around -18°C. Hence, time is required for the ice to reach thermal equilibrium with liquid water (0°C).
11. The Joule effect bias is reduced by taking a 100 microseconds measurement \[4\] every 1 second (0.01% of the time). For a 10 kOhm thermistor connected to 3.3V tension divider, the average dissipated power is 0.01 microwatts. This value is negligible compared to other sources of error, and is therefore not taken into account.
12. Testing several probes simultaneously will increase the thermal leak through the wires, and could reduce the accuracy and stability of the ice bath temperature. We recommend separating as much as possible the probes from each other. The same should apply to wires. This was taken into account in the design of the Jericho Probe Holder. We also suggest using smaller wires to reduce the thermal leak magnitude. Calibrating multiple probes at the same time can increase the time required to stabilize the temperature reading.
13. Extension wires should be as short as possible to minimize the effect of electromagnetic noise. Electromagnetic noise from the environment should also be minimized. We therefore recommend that the user does not extend the lead wires during the calibrations procedures. All noise filters should also be disconnected.
14. The test vessel should not be made of glass. Glass is not transparent to the infrared spectrum, but it is transparent to the visible spectrum. Hence, the probe could absorb some radiant energy in the visible spectrum. This energy gain would bias the temperature measurement.
15. The use of larger ice cubes would create a less uniform temperature bath, which is a source of error. The ice cubes will also tend to melt together more easily due to the larger amount of latent energy available to solidify the water in between the cubes.
16. It is normal that during measurements, the probe temperature will fluctuate slightly (see Figure 4). At least two phenomena are involved. First, the temperature equilibrium is not perfect since it is the microscopic temperature differences combined with Brownian movement that drives the phase change. Second, it is possible that the resistance value of the probe falls in between two values on the ADC, due to its limited accuracy. Both electrical and thermal fluctuations will make the reading oscillate between the two values. These two phenomena are dealt with by averaging the data over a sufficient time period.
17. The overall accuracy of a calibrated sensor depends on the accuracy of the reference point but also on the accuracy of the measurement device used for the calibration procedure. In our lab, the resistance value is measured with the 16-bit accuracy of the ADS1115 (RDL). If you reproduce this experiment at home with the native 10-bit ADC of the RDL, the accuracy of procedure will be lower.
18. The extension wires should be as short as possible to minimize the noise (electromagnetic induction). Electromagnetic noise emanating from the environment should also be minimized, if possible.
19. If you have insufficient quantities of small cubes, the impact of using larger cubes can be minimized by using small cubes in the bottom of the vessel and larger cubes at the top, further away from the probes. In such a scenario however, the accuracy of the bath could be lower.
20. During the measurements, one option is to let the probe still. Alternatively, some users will keep stiring slowly to make sure that all the water and the ice come into intimate contact. Stir in the center region, avoiding the sides, the top and the bottom, where the temperature is different due to heat losses.
21. If you were to replicate the procedure using shaved ice made of distilled water, the uncertainty would be 0.002°C (ASTM E563-11 (2016)).
22. Keep your calibration logs for future consultations. Record keeping is an essential component of any calibration program.
23. Calibration procedures are delicate procedures and it may take a few tries before mastering the procedure. If you are unsure of the results, the procedure should be repeated to see if, at least, you get consistent results.
24. To avoid the ‘stem effect’ during calibration, the Fluke company suggests an immersion depth of 20 times the sum of the probe diameter and the probe length.

**References**

1. ASTM E563-11 (2016) Standard Practice for Preparation and Use of an Ice-Point Bath as a Reference Temperature.
2. ASTM Specification D1193 Standard Specification for Reagent Water.
3. NIST, User-Friendly Guidance on the Replacement of Mercury Thermometers, 2010  https://www.epa.gov/sites/default/files/2015-10/documents/nistuserfriendlyguide.pdf

**Images**
<figure>
<p align="center">
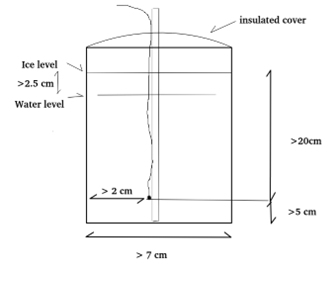
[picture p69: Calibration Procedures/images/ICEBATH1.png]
  
</figure>
    
<p align="center">Schematic of the distance requirements for the ice bath procedure.

<figure>
<p align="center">
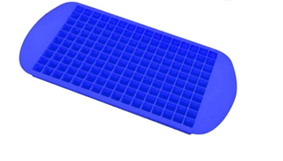
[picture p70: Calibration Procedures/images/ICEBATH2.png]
  
</figure>
<p align="center"> Example of a silicon mold for small ice cubes sold on Amazon

<figure>
<p align="center">
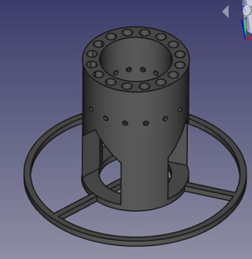
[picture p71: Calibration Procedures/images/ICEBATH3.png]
  
</figure>

<p align="center">Jericho probe holder for cold ice bath (revB4)

<figure>
<p align="center">
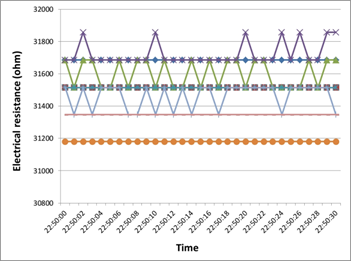
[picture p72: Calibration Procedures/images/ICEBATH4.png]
  
</figure>
<p align="center">Typical data for a measurement period of 30  
seconds in an ice bath with a probe holder for 8 probes.

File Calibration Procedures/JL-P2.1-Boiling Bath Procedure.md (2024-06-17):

JL-P2.1 - Boiling Bath (Steam Point) Procedure
=================================
by Jericho Lab

This procedure will produce a steam point close to 100°C (212°F). The exact temperature depends on the atmospheric pressure. The steam point is used to ensure that the temperature measurement reflects the properties of steam rather than the liquid water, as steam provides a more stable reference temperature under constant pressure conditions. Liquid water might be superheated or subject to other thermal phenomena.

The procedure is based on  NIST Special Publication 250-23 (1988) as well as more recent comments from the NIST. This point is also referred as the “steam point”. This method can achieve an uncertainty of 0.1°C (0.2°F) at a 95 % confidence level. The procedure is part of our three-point calibration. The procedure can be replicated by the user to verify the calibration of the system over time.

**WARNING**: This procedure uses boiling water and generates hot steam. DO NOT move a vessel filled with fluid. Protect yourself from burns and scalding. Jericho Laboratory Inc. is not responsible for any damage or your safety if you attempt to reproduce this procedure.

**Required material**

- Stainless steel pot (minimum dimensions: 20 cm dia. x 20 cm (8 x 8 inches))
- One aluminum plate (minimum bottom dimension: 18 cm diameter (7 inches))
- Scissors
- Tap water
- Clean thermistor probe with wire
- Plastic stick
- Third-hand or clothes clamp
- Hot plate (heat source)

**Procedure**

1. Connect all the uncalibrated probes to the data logger and activate your RDL data logger. Make sure that the printing of the resistance values is activated. These values will be the basis of the calibration calculations.
2. Wash the pot and the probe with soapy water and rinse three times with tap water.
3. Attach the probe on the plastic stick and hold the plastic stick with the third-hand.
4. Using the scissors create a hole in the aluminum plate, large enough for the stick.
5. Fill the pot with 10 cm (4 in.) of clean tap water.
6. Put the aluminum lid on and bring water to a strong boil.
7. Once the water boils, lower the heat but boiling should remain strong during measurements.
8. Insert the probe into the pot. The probe should be 2 cm above the water level \[NIST\]. There should be 10 to 15cm (4 to 6 in.) of the thermometer/wire immersed in the space where the steam collects.
9. Determine the atmospheric pressure (barometric pressure) at your position. Be as precise as possible (ex: 1013 hPa). If you use data from a local weather station, the station should be as close as possible from your location and be less than one (1) hour old. For example, the weather station in Montreal (airport) is 13 km from the Jericho lab, a relatively small distance as far as atmospheric pressure is concerned.
10. The probe must be exposed to five (5) minutes of rolling boil before taking measurements \[NIST\].
11. Measure the electrical resistance every second for 30 seconds, one time per second. See Figure 1 for a typical curve.
12. Data treatment: Calculate the atmospheric pressure and average the 30 data points.
13. NIST: The uncertainty of the elevation limits the uncertainty of the steam point. Using the steam point calculator, you can achieve an uncertainty of 0.1 °C (0.2 °F) at a 95 % confidence level. The steam point equation is given by the NIST Excel sheet referenced at the end of this document. Pressure must be between 97.0 and 104.0 kPa for the equation to be valid.
14. Keep your calibration logs for future consultations. Record keeping is an essential component of any calibration program.
15. Calibration procedures are delicate procedures and it may take a few tries before mastering the procedure. If you are unsure of the results, the procedure should be repeated to see if, at least, you get consistent results.
16. To avoid the ‘stem effect’ during calibration, the Fluke company suggests an immersion depth of 20 times the sum of the probe diameter and the probe length.

 <figure>
  <p align="center">
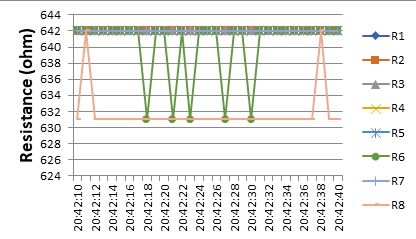
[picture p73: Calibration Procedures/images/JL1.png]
   
 </figure>
 <p align="center"> Typical data for a measurement period of 30 seconds in a boiling bath with a probe holder for 8 probes.

<p align="center"> 
 Table 1 Frequent values as per the NIST Excel sheet.
 
<figure>
 <p align="center">
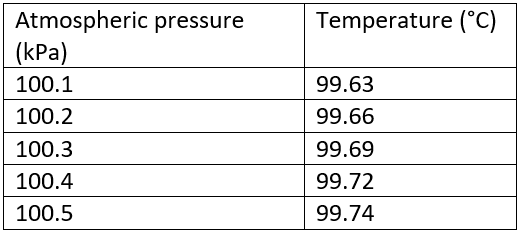
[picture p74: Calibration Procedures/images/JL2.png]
   
</figure>

**Comments**

1. The lid is absolutely necessary to get accurate results. The steam accumulates within the pot and creates a slight positive pressure. This way no cold surrounding air enters the pot.
2. The NIST recommends using a pot that is at least 8 inch deep.
3. Be careful that no bare metal from the probe is exposed to the steam. It could cause a measurement error by electrical conductivity.
4. To reduce thermal leaks through the lead wire, we recommend keeping as much lead wire inside the cavity as possible.
5. Our data comes from the Montreal Airport, which is at the same altitude as the laboratory. There is therefore no need to correct for altitude. If you reproduce this procedure, you might have to account for elevation (ex: United States Geological Survey website). The building height is taken into account (see calibration certificate for an example).
6. You might need a few tries to figure out what level of heat will maintain a rolling boil. Do not remove the lid during the measurements.
7. There is no need to use distilled water. The steam produced is in itself a small distillation process. For the same reason, gloves are not necessary.
8. At the interface where the water meets the steam, the temperature should theoretically be the same, as both the water and the steam are at the boiling point under given atmospheric conditions. However, placing the probe above the water level ensures that it measures the temperature of the steam exclusively, without the potential interference or variability that might occur if the probe were to touch the water. This method provides a more controlled environment to accurately gauge the steam's temperature.
9. To find recent atmospheric pressure data near you, we suggest the National Weather Service website (USA) or Environment Canada (Canada). NIST recommends using data that is at maximum one hour old.
10. When using a thermistor probe, the Joule effect bias is reduced by taking a 1 mS measurement every 1 second.
11. The overall accuracy of a calibrated sensor depends on the accuracy of the reference point but also on the accuracy of the measurement device used for the calibration procedure. In our lab, the resistance value is measured with the 16-bit accuracy of the ADS1115 (RDL). If you reproduce this experiment at home with the native 10-bit ADC of the RDL, the accuracy of procedure will be lower.
12. It is possible to test more than one probe at the same time. However, this will increase the thermal leak through the wires, and could reduce the accuracy and stability of the ice bath temperature. We recommend separating as much as possible the probes from each other. The same should apply to wires. We also suggest using smaller wires to reduce the thermal leak magnitude. Calibrating multiple probes at the same time can increase the time required to stabilize the temperature reading.
13. The extension wires should be as short as possible to minimize the noise (electromagnetic induction). Electromagnetic noise emanating from the environment should also be minimized, if possible.

**References**  
Certain commercial equipment, instruments or materials are identified in this paper in order to adequately specify the experimental procedure. 

- NIST Special Publication 250-23 (1988)  
https://nvlpubs.nist.gov/nistpubs/Legacy/SP/nistspecialpublication250-23.pdf  
- NIST, User-Friendly Guidance on the Replacement of Mercury Thermometers, 2010  https://www.epa.gov/sites/default/files/2015-10/documents/nistuserfriendlyguide.pdf
- Natural Resources Canada (Canada weather data)  
<https://weather.gc.ca/past_conditions/index_e.html?station=yul>
- National Weather Service (USA weather data)  
<https://www.weather.gov/>
- NIST Procedure for steam point:  
<https://www.nist.gov/pml/mercury-thermometer-alternatives/mercury-thermometer-alternatives-verification-methods>

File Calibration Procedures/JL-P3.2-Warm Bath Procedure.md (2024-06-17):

­JL- P3.2 – Warm Bath Reference Procedure
========================================
by Jericho Lab  

**WARNING**: Jericho Laboratory is not responsible for any damage or your safety if you attempt to reproduce this procedure. DO NOT move a vessel filled with fluid. Underneath the jug lid, the Coleman Company indicates that the jug model 6009 should not be used for hot liquids. Use this jug at your own risk. We advise that you find an alternative product that is designed for hot liquids.

**Technical description**

This procedure allows the creation of a reference temperature for a liquid bath between 35 and 40°C, with an accuracy of +/- 0.2°C. This procedure is part of our three-point calibration process for thermistors. It can be replicated by the user - at their own risk - to verify the calibration of probes. The procedure makes uses of a waterproof (IP67) ovulation thermometer (BIOS 16C2). Other popular brands could possibly work as well, with some verifications.

This procedure is not based on any standard procedure, but it is inspired by the NIST documentation (“Room Temperature Verification”) and ASTM E2488-09 (Standard Guide for the Preparation and Evaluation of Liquid Baths Used for Temperature Calibration by Comparison).

An ovulation thermometer is normally used to monitor the body temperature of women in order to characterize their ovary cycle and enhance pregnancy likelihood. Due to its medical use, the ovulation thermometer is a reliable product, with high resolution (0.01°C) and good accuracy (+/- 0.1°C) in a limited temperature range (34 to 42°C). As the analog-to-digital (ADC) converter is being applied to a narrow range of temperatures, the uncertainty related to numeric conversion is reduced. This is one of the reasons why such an accurate thermometer can be acquired at a low price. Being mass produced and consumer grade, these types of thermometers are affordable ($15-30) and can be found in drugstores.

The overall logic of the procedure is to use the highly-precise ovulation thermometer as a reference thermometer within a liquid bath. The system is not thermally static: it is slowly cooling towards room temperature (exponential curve). However, it can be linearized if we consider a very small section of the curve (<0.1 °C). The water temperature will have changed slightly between the reference measurement and the probe measurement. To compensate that effect, a second reference reading is done at the end \[NIST\]. The two reference readings are averaged to form the final reference value. The final measurement value for the uncalibrated probe is an average of the 30 measurements sequence. This is illustrated in Figure 1, where a set of only 2 (not 30) measurements is considered. One downside of this technique is that, since the reference thermometer is used twice, the instrument uncertainty must be considered twice. For more information, please consider reading about uncertainty propagation. This is why this procedure can provide a reference point with an uncertainty of +/- 0.2°C.

<figure>
  <p align="center">
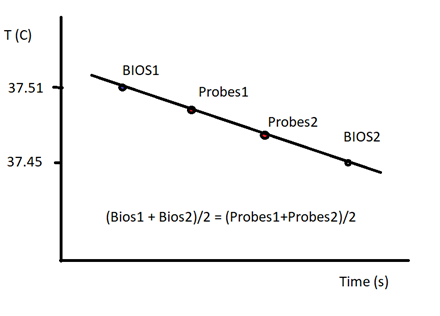
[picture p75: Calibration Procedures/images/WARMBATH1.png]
    
      </p>
</figure>

 <p align="center">Main events in the measurement sequence for the warm bath calibration procedure.

**Required material**

- 1x Insulated vessel with its lid, non-transparent, with at least a 300 mm in height and 70 mm in diameter.
  - e.g. Coleman jug, model 6009, 1/2 gallon (1.9 L).
- 1x Ovulation thermometer,
  - e.g. BIOS model 16C2
- Custom 3D-printed probe holder (see Jericho Github repo)
- 1 piece of closed cell foam insulation (water column insulation)
- 1 to 10 temperature probes, uncalibrated
  - e.g. Jericho thermistors.
- Tap water (at least 2L)

**Procedure**

1. Read the instructions of your thermometer.
2. Connect all the uncalibrated probes to the data logger and activate your RDL data logger. Make sure that the printing of the resistance values is activated. These values will be the basis of the calibration calculations.
3. Start recording the resistance values from the thermistors at 1s interval indefinitely.
4. Clean all equipment with some soapy water. Rinse once with tap water.
5. Position all the uncalibrated probes in the apparatus (i.e. probe holder).
6. Position the apparatus inside the vessel. The wires should go through the lid opening. All probes, including the reference thermometer, should be positioned at the same depth.
7. Fill the vessel with warm water from the sink, leaving space for the lid. The water should be 42-43 °C. You can verify the temperature with your ovulation thermometer.
8. To reduce thermal leaks through the lead wire, we recommend keeping as much lead wire inside the cavity as possible.
9. Add a layer of closed cell foam insulation above the water column and the probes.
10. Put the lid on the vessel for 10 min. This will allow the inner volume to reach spatial thermal equilibrium as much as possible – although the whole system is slowly cooling down towards room temperature. To verify the thermal gradient within the working space, a second identical reference thermometer can be used simultaneously at various locations.
11. Wait until the water temperature cools down to 38-39°C, which is the most accurate range of this type of thermometer (i.e., body temperature)
12. Open the vessel lid.
13. Measure the water temperature a first time with the reference thermometer. You will hear the beeping sound through the water when it has finished. The BIOS thermometer will retain the highest temperature registered.
14. Read the final value from the BIOS thermometer (e.g., 37.21 °C) and write it down. This is value “BIOS1”. Also, write down the time displayed by the RDL, to the exact second.
15. Wait around ten seconds then take a second reading from the reference thermometer.
16. Read the temperature registered by the thermometer (e.g., 37.15 °C) and write it down. This is value “BIOS2”. Also, write down the time displayed by the RDL, to the exact second.
17. Calculate the arithmetic average of BIOS1 and BIOS2. (e.g., (37.21 + 37.15)/2 = 37.18 °C). This value is the reference temperature for the procedure.
18. Save all the data from the data logger to a text file. With as spreadsheet, determine the average resistance value of each probe in the period between BIOS1 and BIOS2.
19. Keep your calibration logs for future consultations. Record keeping is an essential component of any calibration program.

**Comments**

1) A non-insulated vessel will give less accurate results due to a less homogeneous bath temperature.
2) Make sure that no bare metal from the probe wire is exposed to water. The electric conductivity would induce an error in the resistance value measured.
3) In theory, the bath could be replaced by an electrically heated bath, equipped with a thermostat. The magnitude and impact of the thermal fluctuations should be evaluated however.
4) If you do not have access to a probe holder, you can try to approximate the procedure with a substitute. For example, you could tie the probes and the reference thermometer to a plastic ruler. However, the expected accuracy of such modified procedure is unclear.
5) It is not necessary to use distilled water or gloves for this procedure since potential impurities will not affect the temperature evolution of the medium.
6) The thermistor must be immersed deeply enough to avoid perturbation of the temperature by radiation or thermal conduction along the electrical wires. This is why this procedure has a significant water column above the probe.
7) The Joule effect bias is reduced by taking a 100 microseconds measurement \[4\] every 1 second (0.01% of the time). For a 10 kOhm thermistor connected to a 3.3V tension divider, the average dissipated power is 0.01 microwatts. This value is negligible compared to other sources of error, and is therefore not taken intoaccount.
8) It is possible to test 1 to 16 probes at the same time. However, this increases the thermal leak through the wires, and can reduce the accuracy and stability of the bath temperature. We recommend separating as much as possible the probes from each other. The same should apply to wires. We also suggest using smaller wires to reduce the thermal leak magnitude. Calibrating multiple probes at the same time can increase the time required to stabilize the temperature reading.
9) The test vessel should not be made of glass. Otherwise, the probe could absorb some radiant energy in the visible spectrum. This would bias the temperature measurement.
10) During measurements, the probe temperature oscillations are considered normal. This is the reason why we average.
11) For even more precision, a plastic structure could be inserted to reduce the convection within the column of liquid, leaving a hole in the center for the probes.
12) Many beverage jugs, such as the Coleman 6009, do not have an insulated lid. This causes an increased overall heat loss as well as increase natural convection, since the cooling occurs on top of the liquid column. To reduce these effects, we add a layer of closed cell foam insulation above the water column. 
13) Calibration procedures are delicate procedures and it may take a few tries before mastering the procedure. If you are unsure of the results, the procedure should be repeated to see if, at least, you get consistent results.
14) To avoid the ‘stem effect’ during calibration, the Fluke company suggests an immersion depth of 20 times the sum of the probe diameter and the probe length.
15) Extension wires should be as short as possible to minimize the effect of electromagnetic noise. Electromagnetic noise from the environment should also be minimized. We therefore recommend that the user does not extend the lead wires during the calibration procedures. All noise filters should also be disconnected.

<figure>
  <p align="center">
    
</figure>
<p align="center">
Warm bath apparatus: 3D-printed probe holder (thermal equalizing block)

**Thermometer BIOS 16C2 specifications (as per manufacturer)**  
Storage temperature: -25℃ to +55℃/ 15% to 95% HR  
Operating environment: 10℃ to 40℃/15% to 95% HR  
Measurement Range: 32.00°C to 42.99°C  
Measurement Accuracy: +/- 0.1°C between 34°C and 42°C  
Smallest Display Unit: 0.01°C  
Memory: Stores last measurement  
Battery lifetime: approx. 4500 measurements  
Expected service life: 5 years  
IEC 60601-1-11 (Part 1 of norm 60601, edition 2011)

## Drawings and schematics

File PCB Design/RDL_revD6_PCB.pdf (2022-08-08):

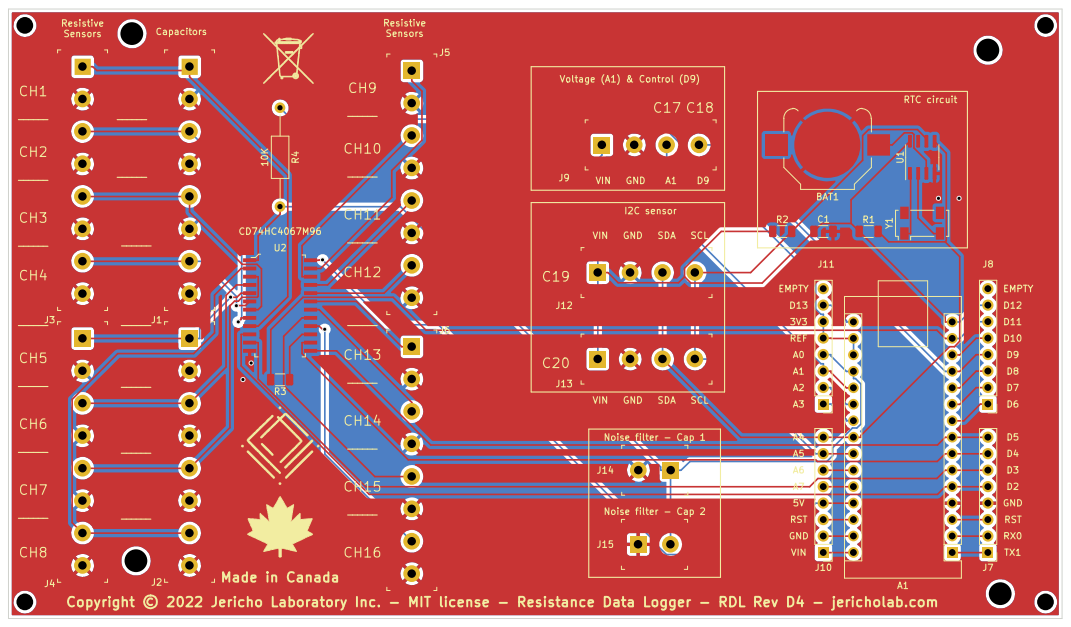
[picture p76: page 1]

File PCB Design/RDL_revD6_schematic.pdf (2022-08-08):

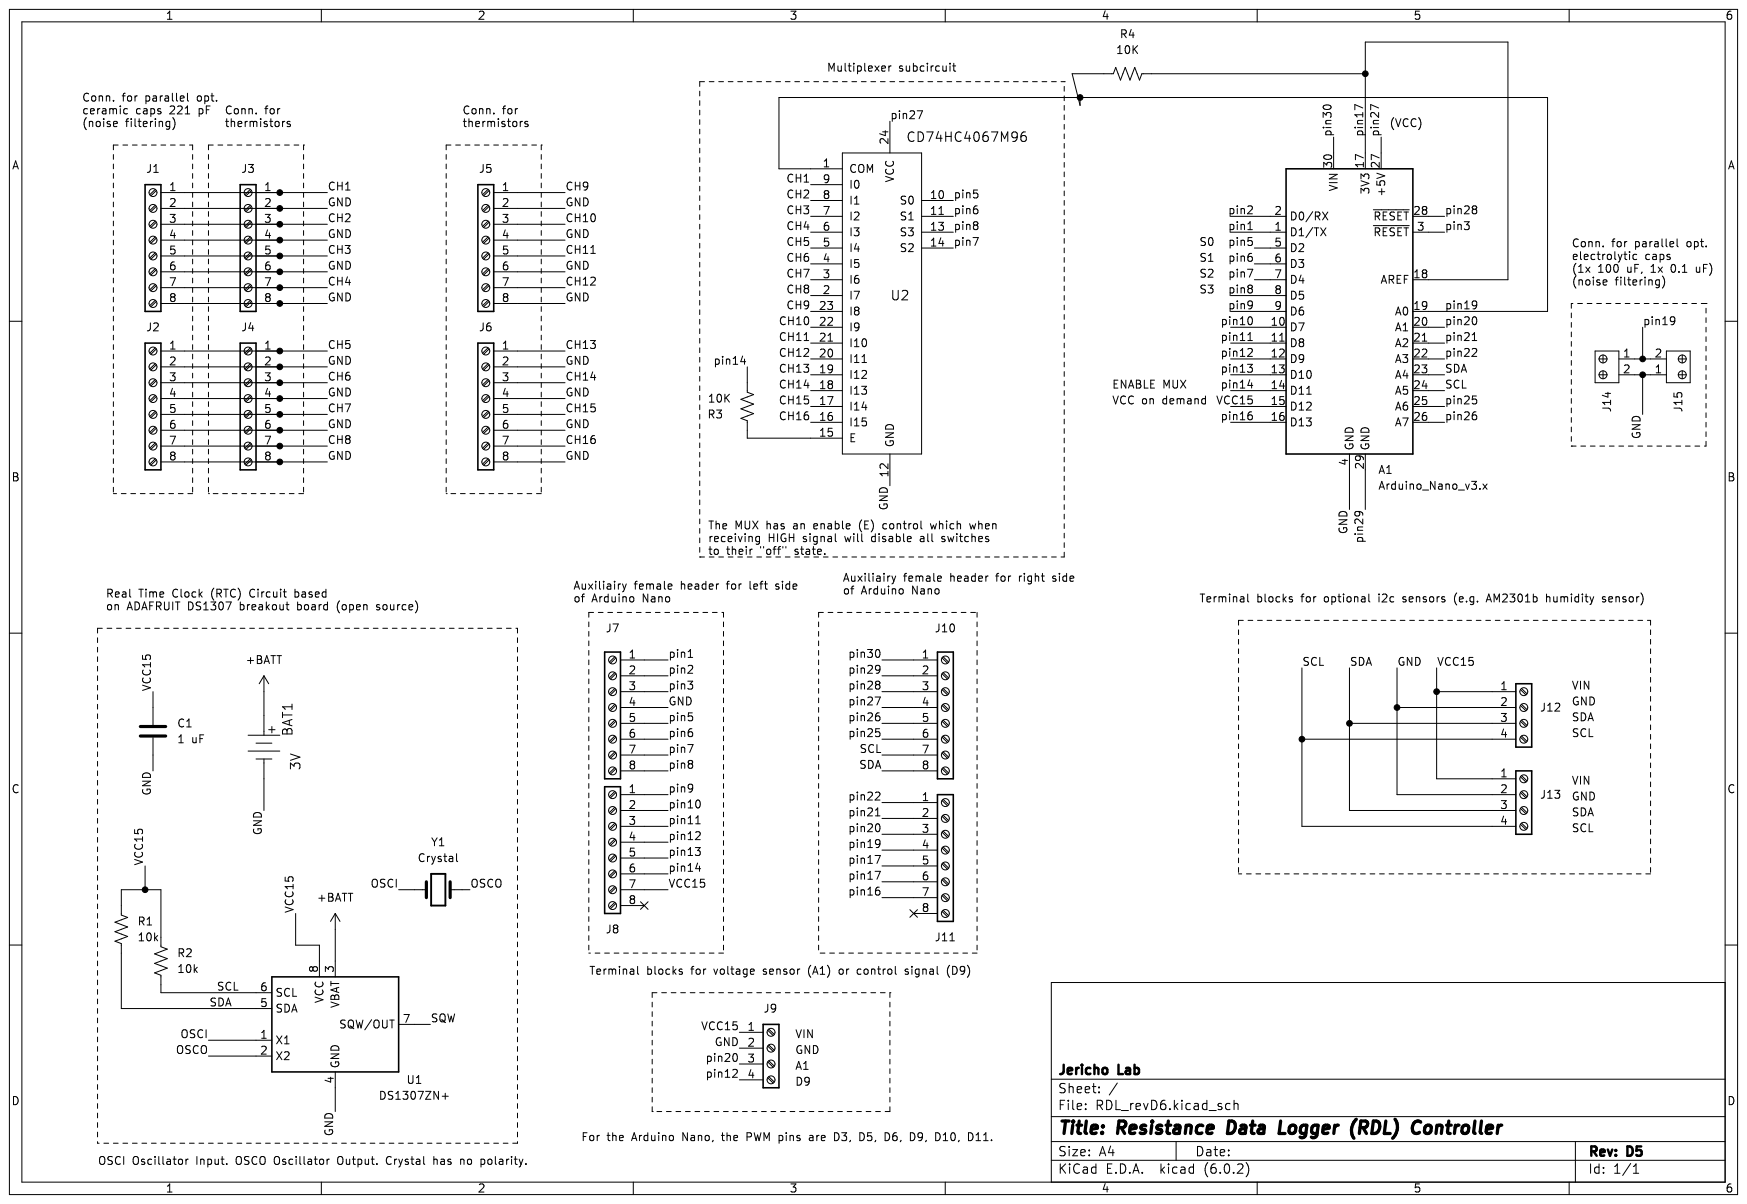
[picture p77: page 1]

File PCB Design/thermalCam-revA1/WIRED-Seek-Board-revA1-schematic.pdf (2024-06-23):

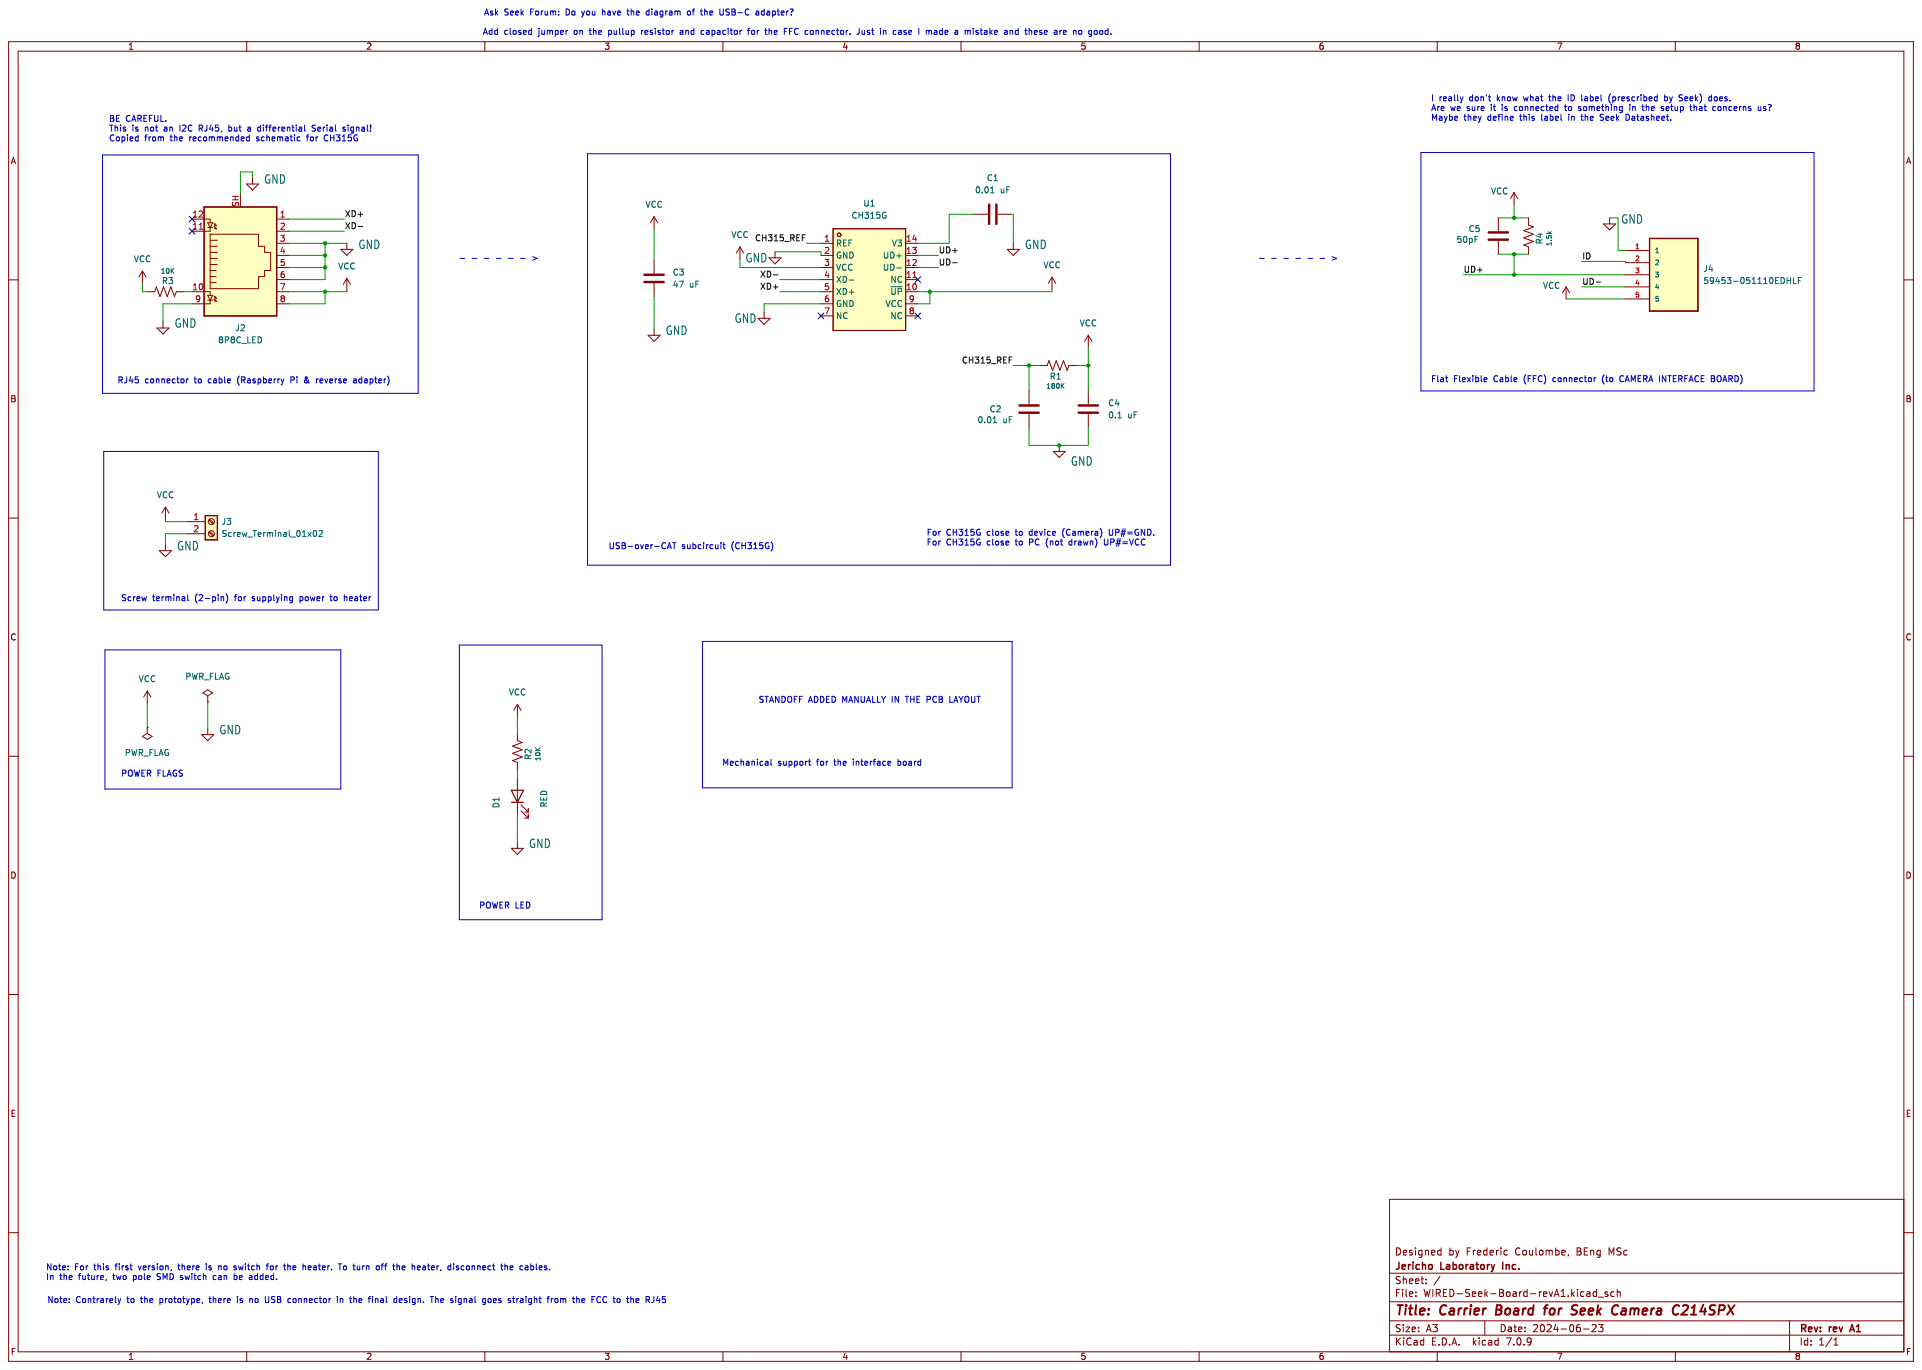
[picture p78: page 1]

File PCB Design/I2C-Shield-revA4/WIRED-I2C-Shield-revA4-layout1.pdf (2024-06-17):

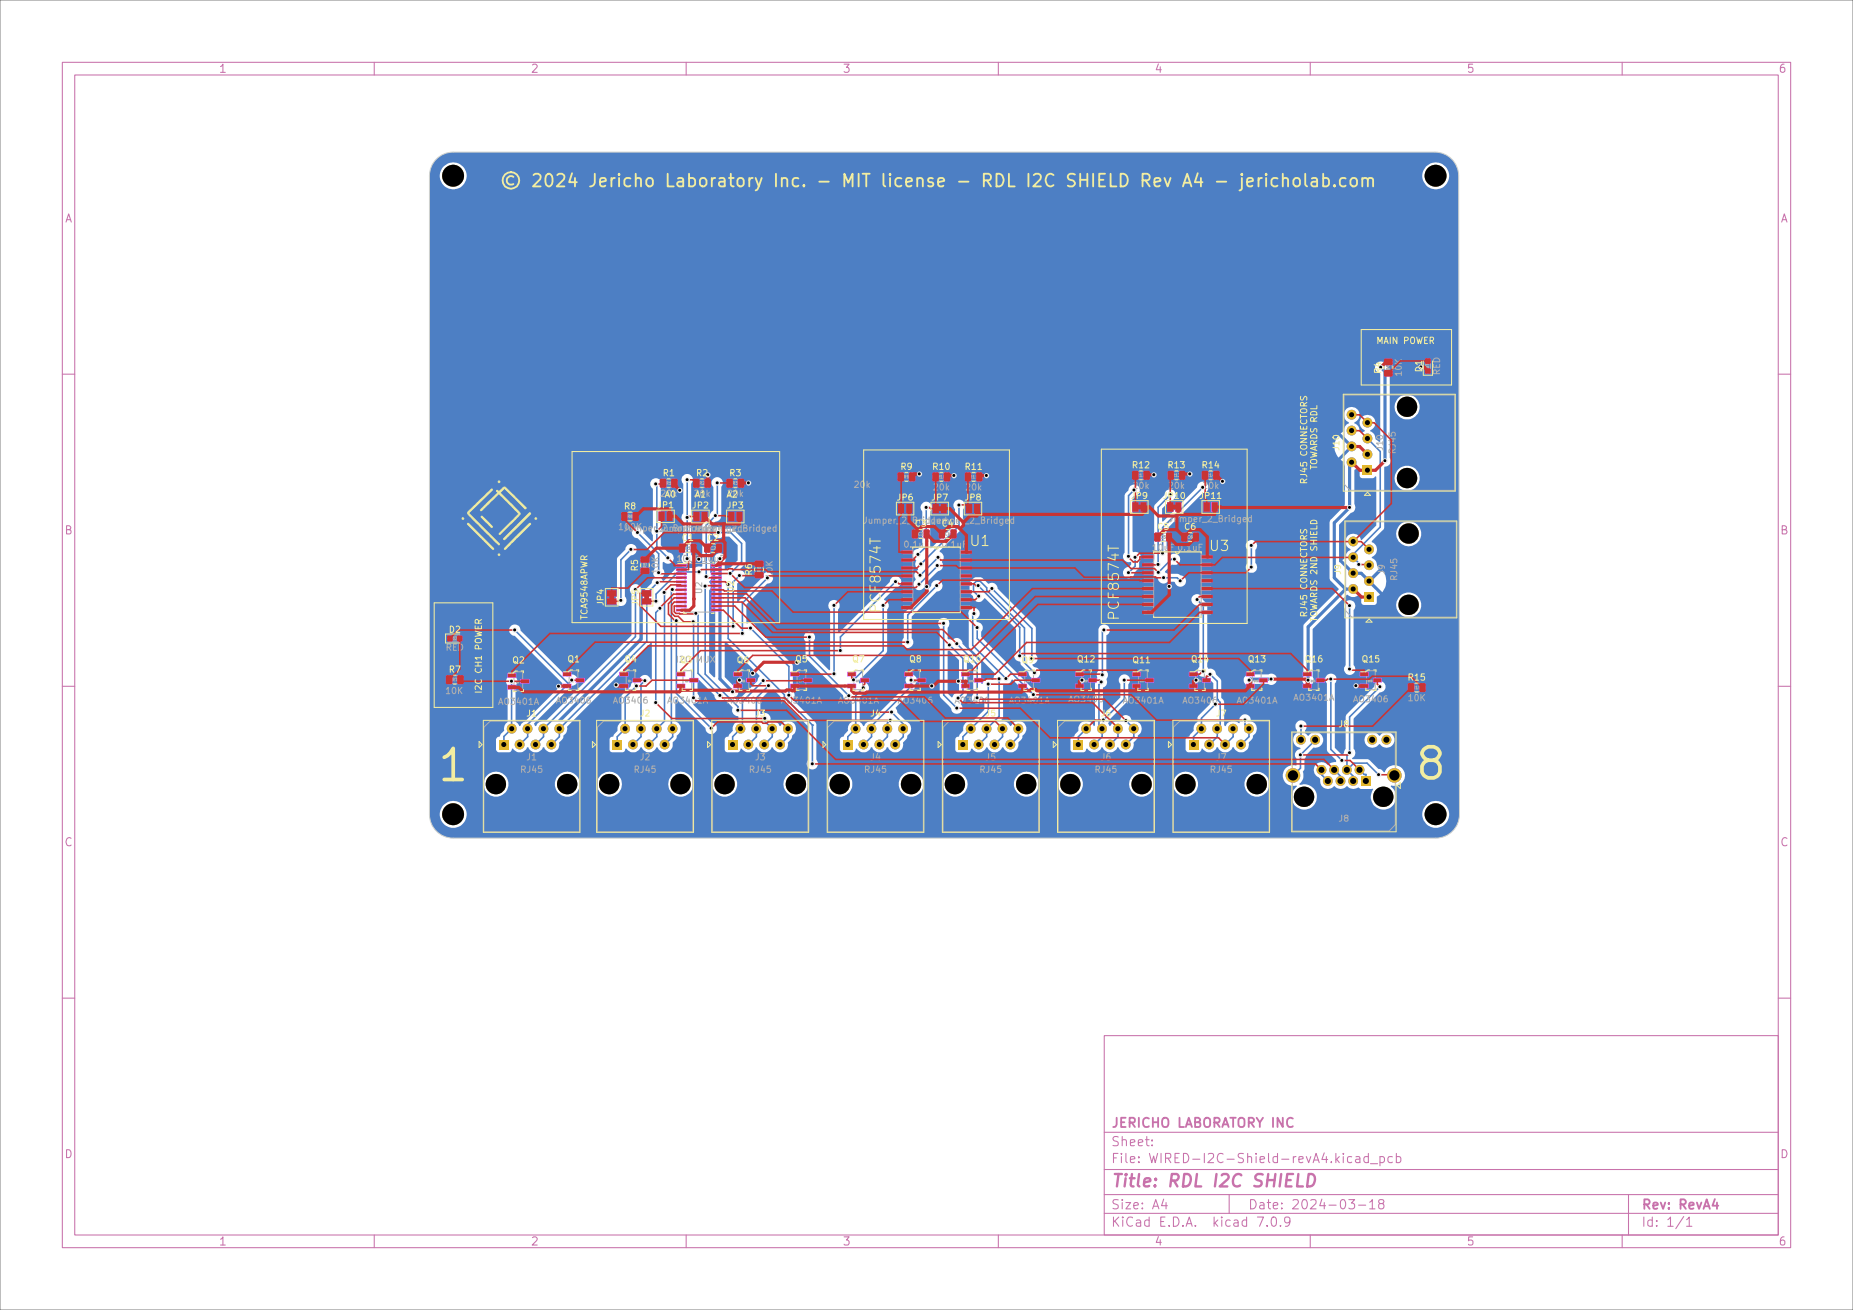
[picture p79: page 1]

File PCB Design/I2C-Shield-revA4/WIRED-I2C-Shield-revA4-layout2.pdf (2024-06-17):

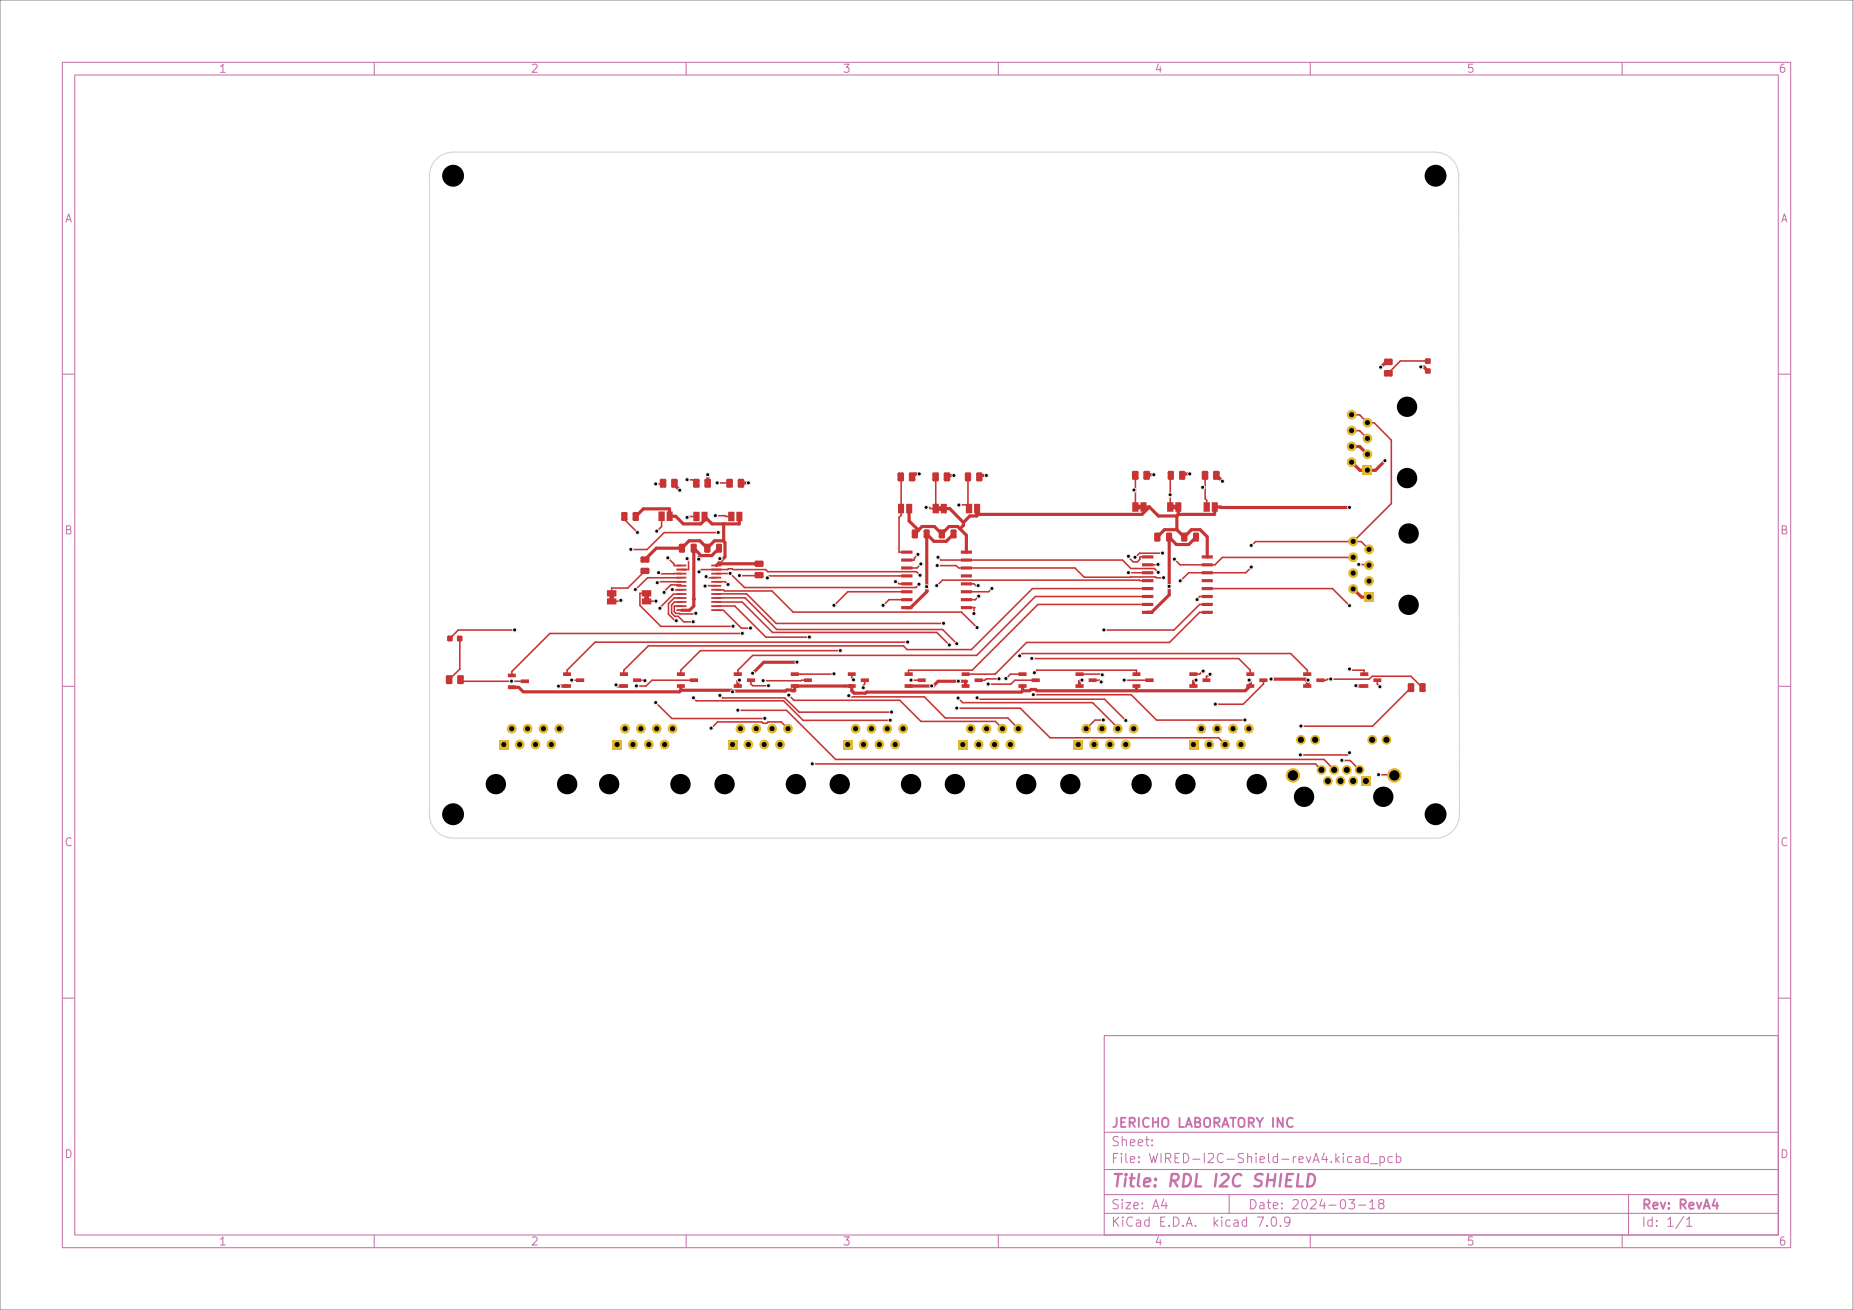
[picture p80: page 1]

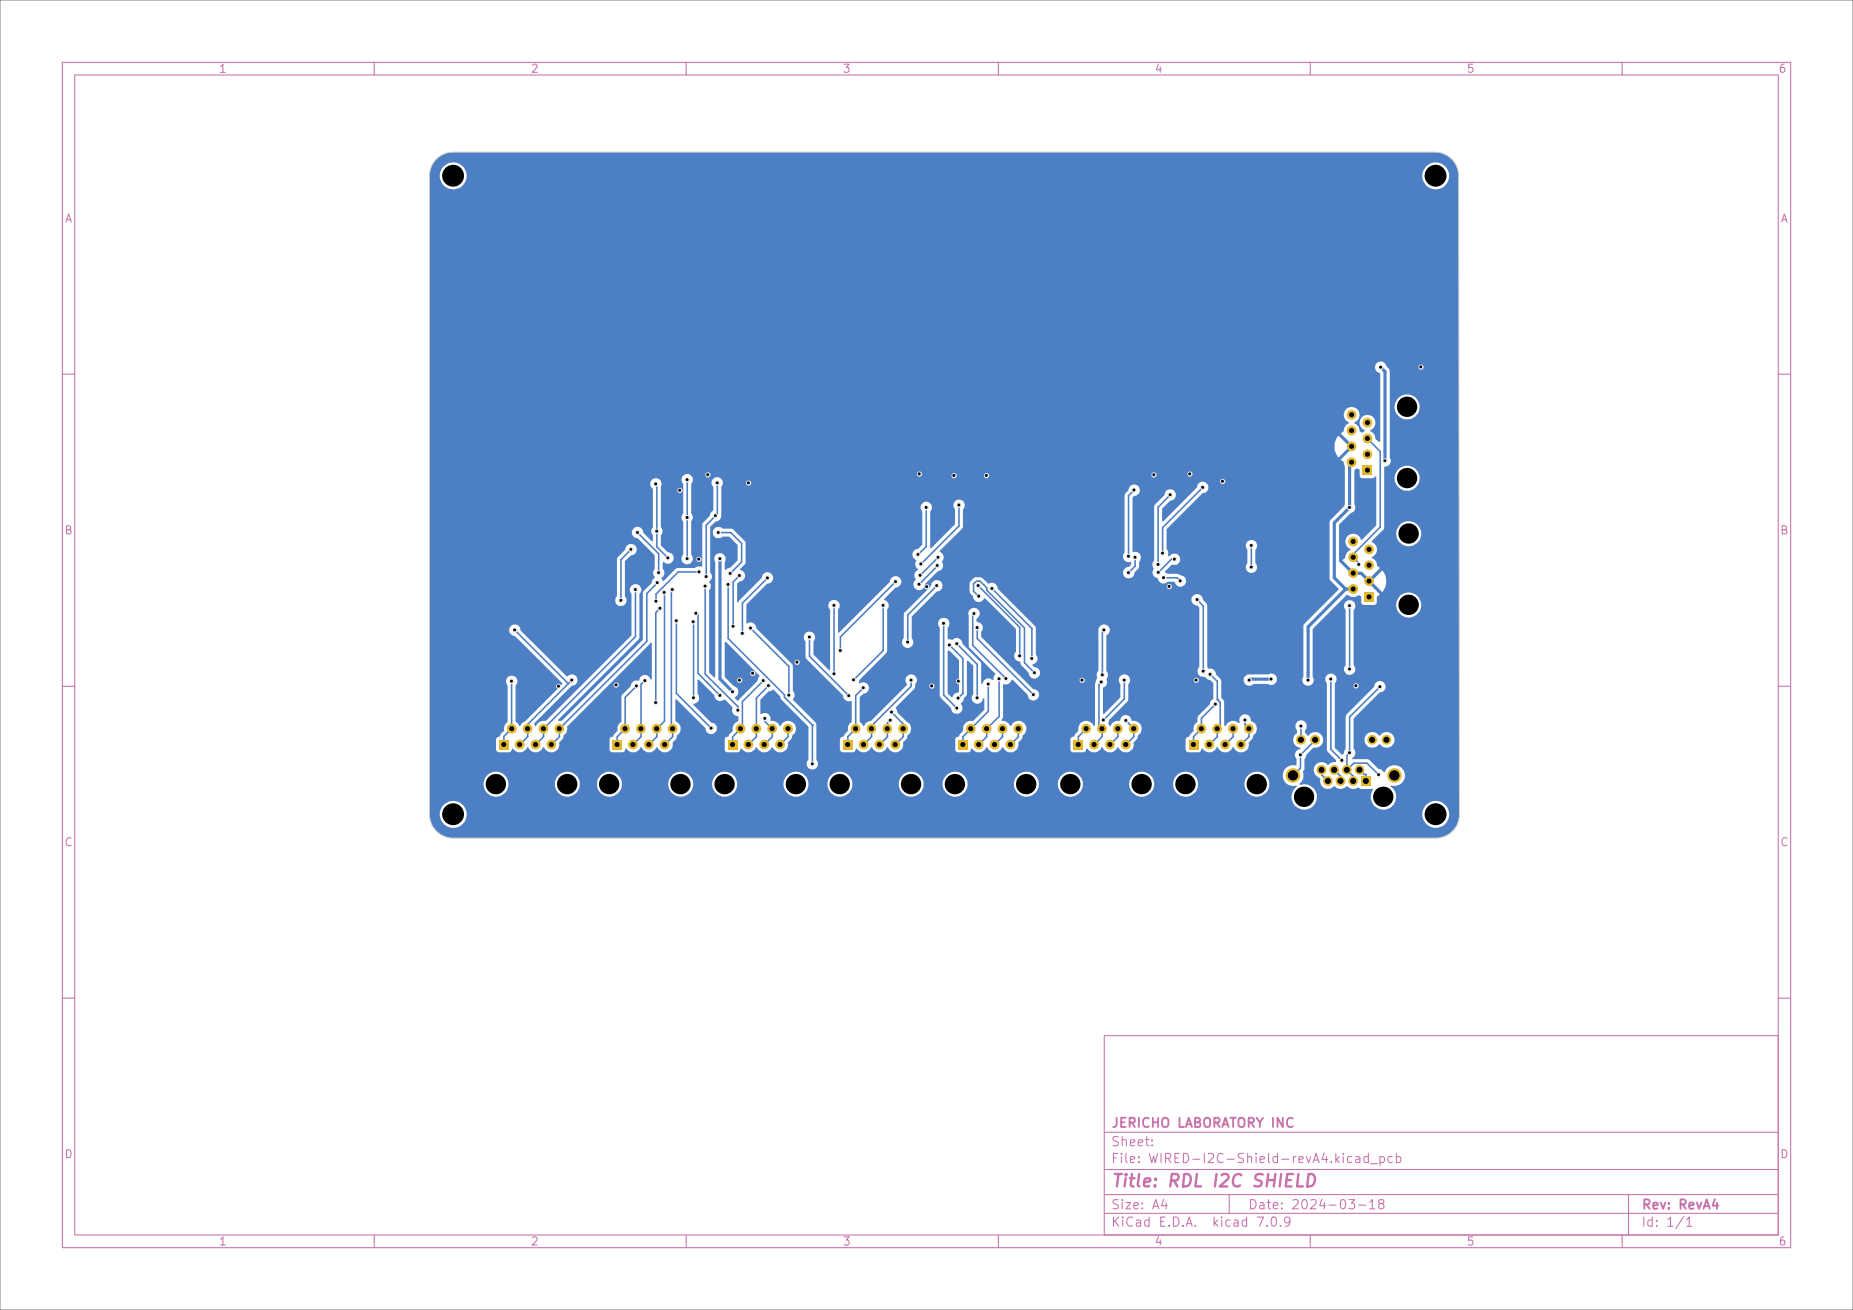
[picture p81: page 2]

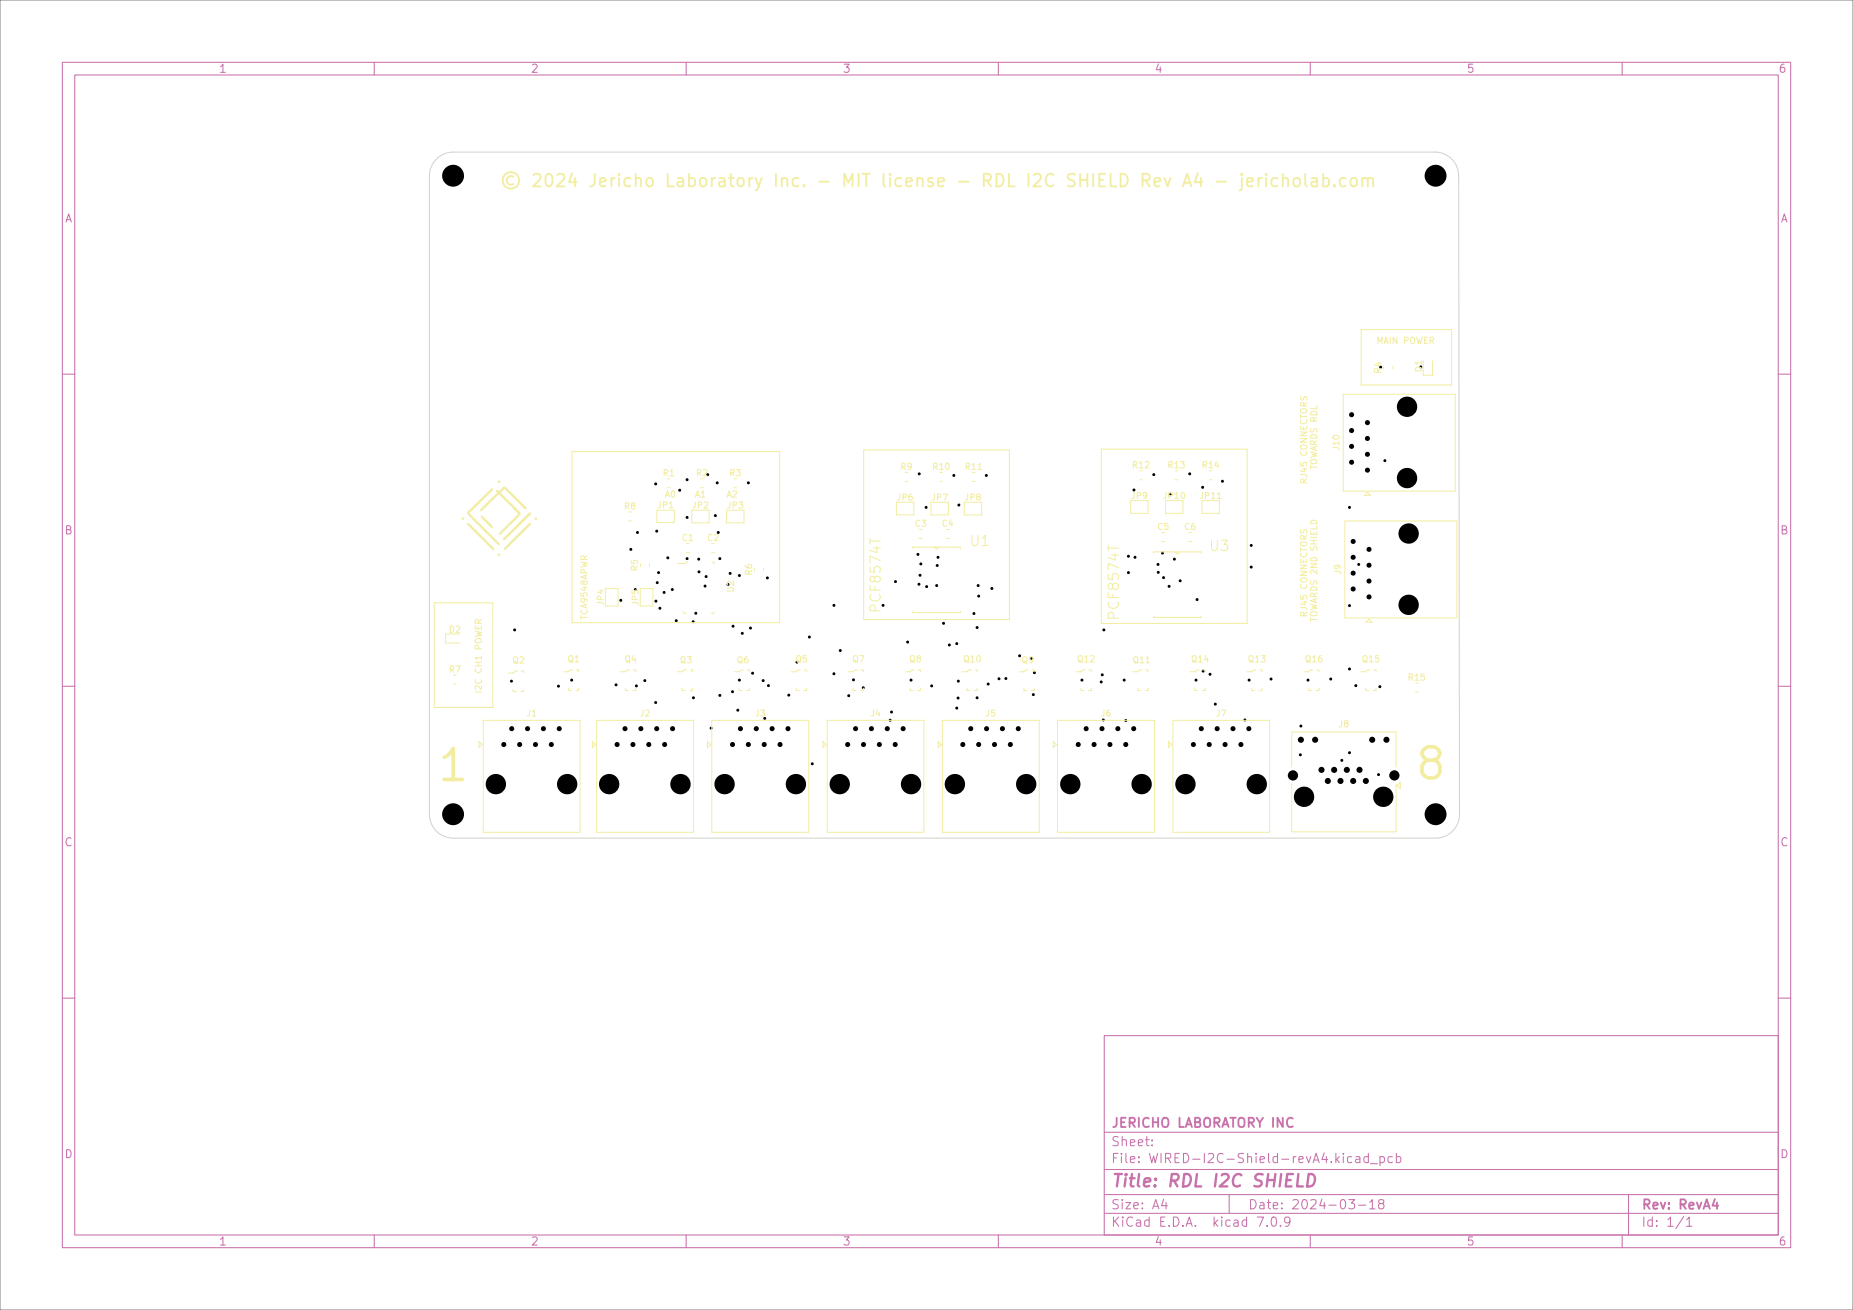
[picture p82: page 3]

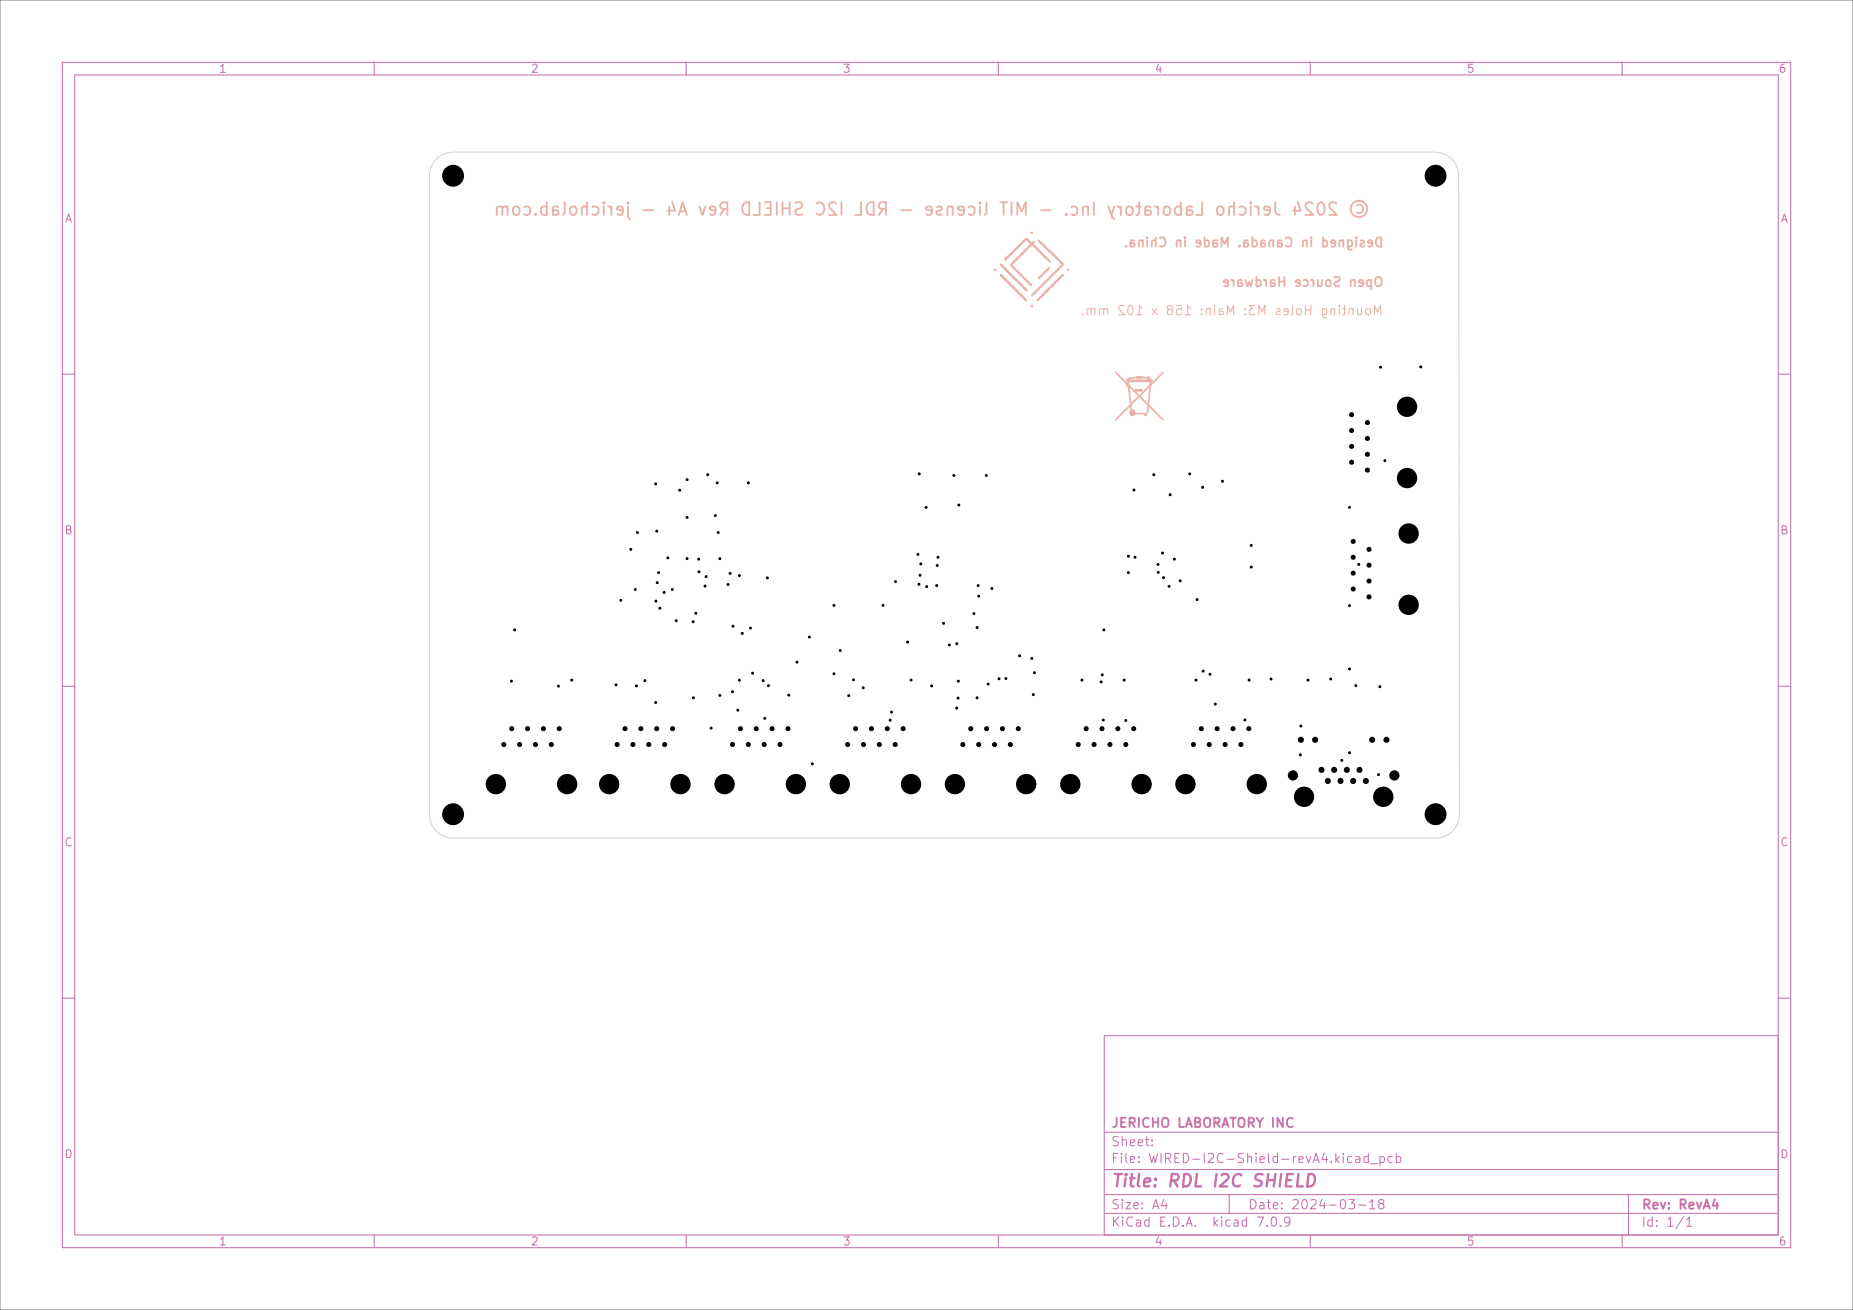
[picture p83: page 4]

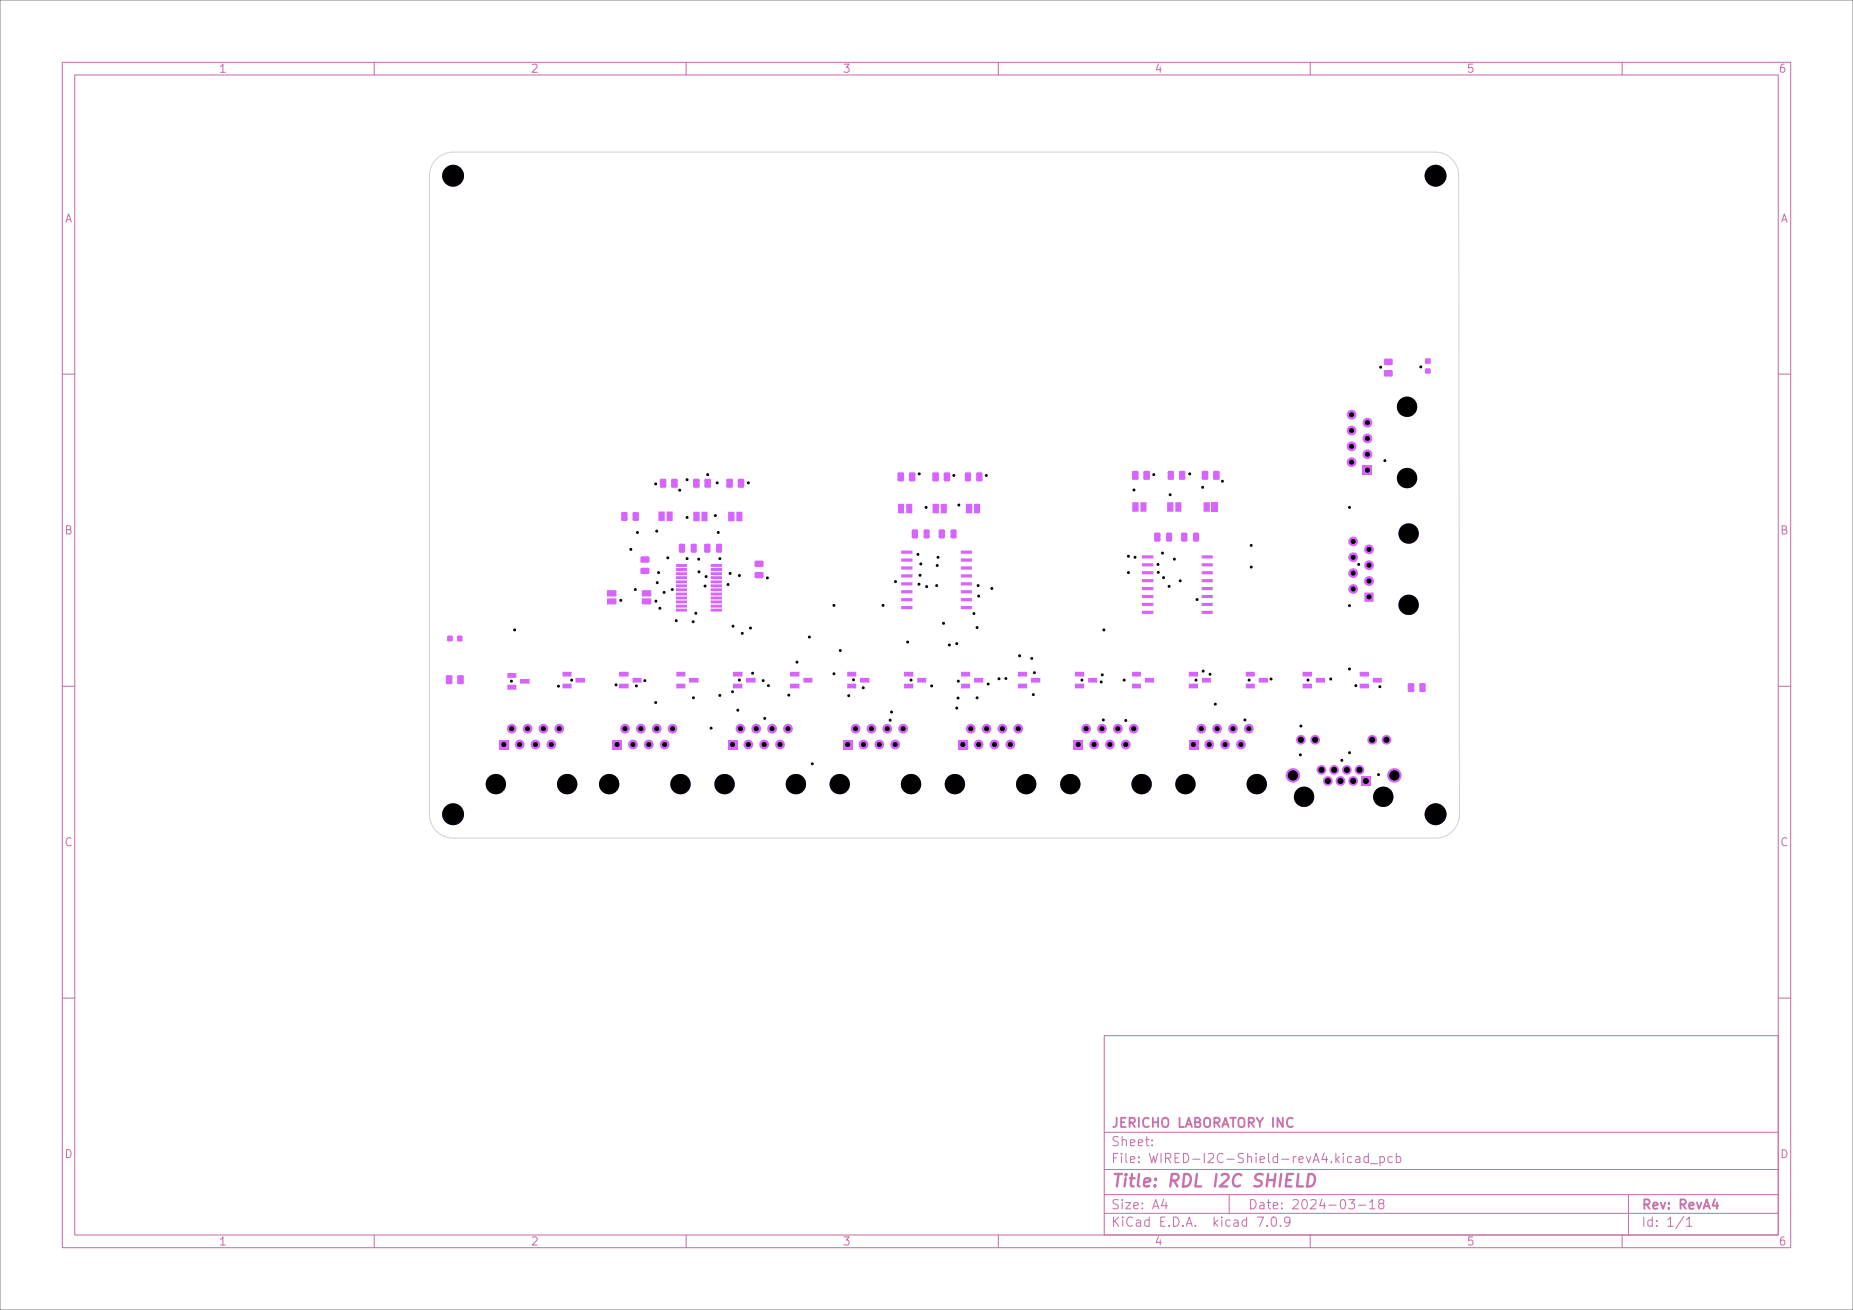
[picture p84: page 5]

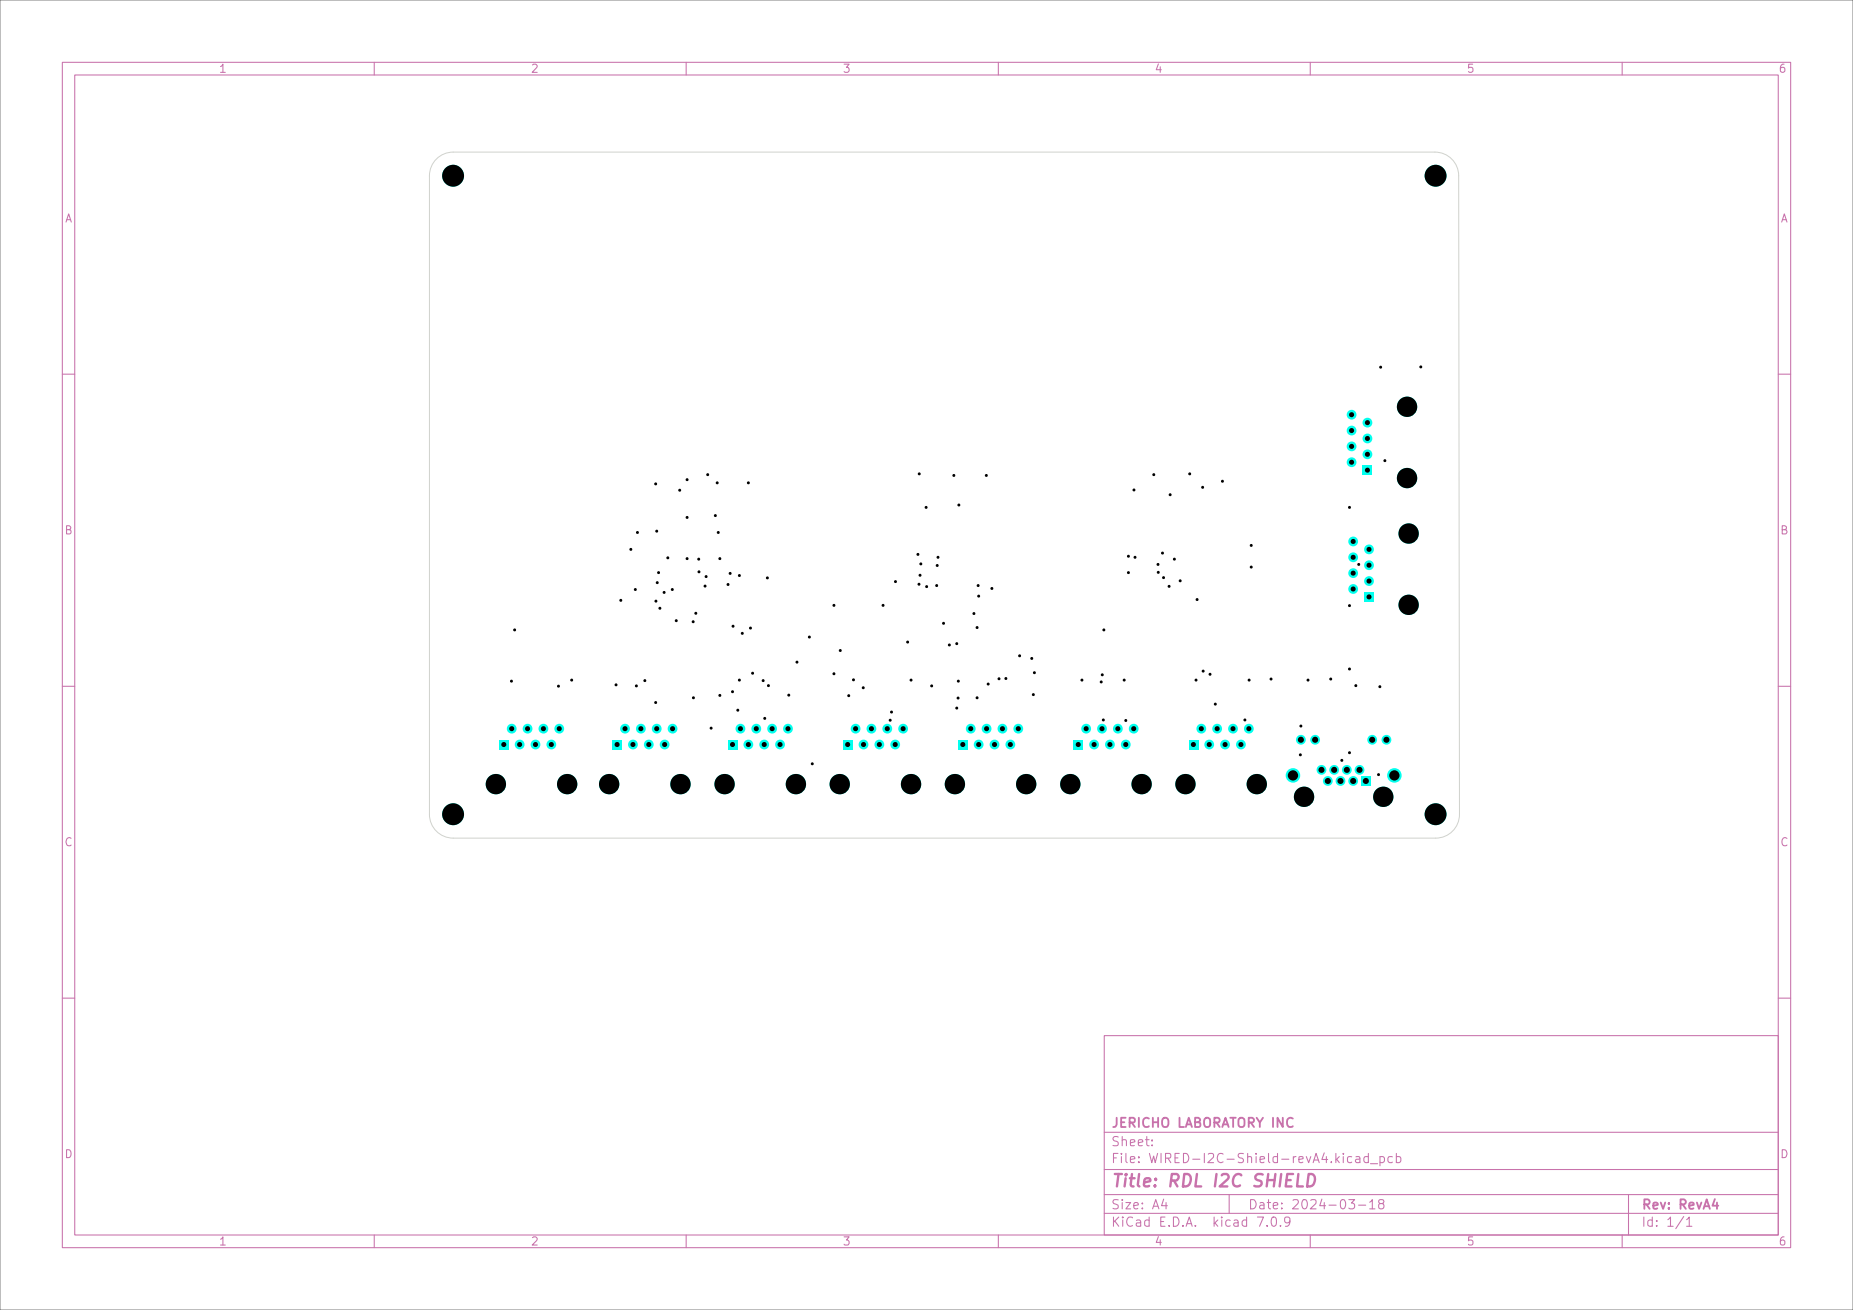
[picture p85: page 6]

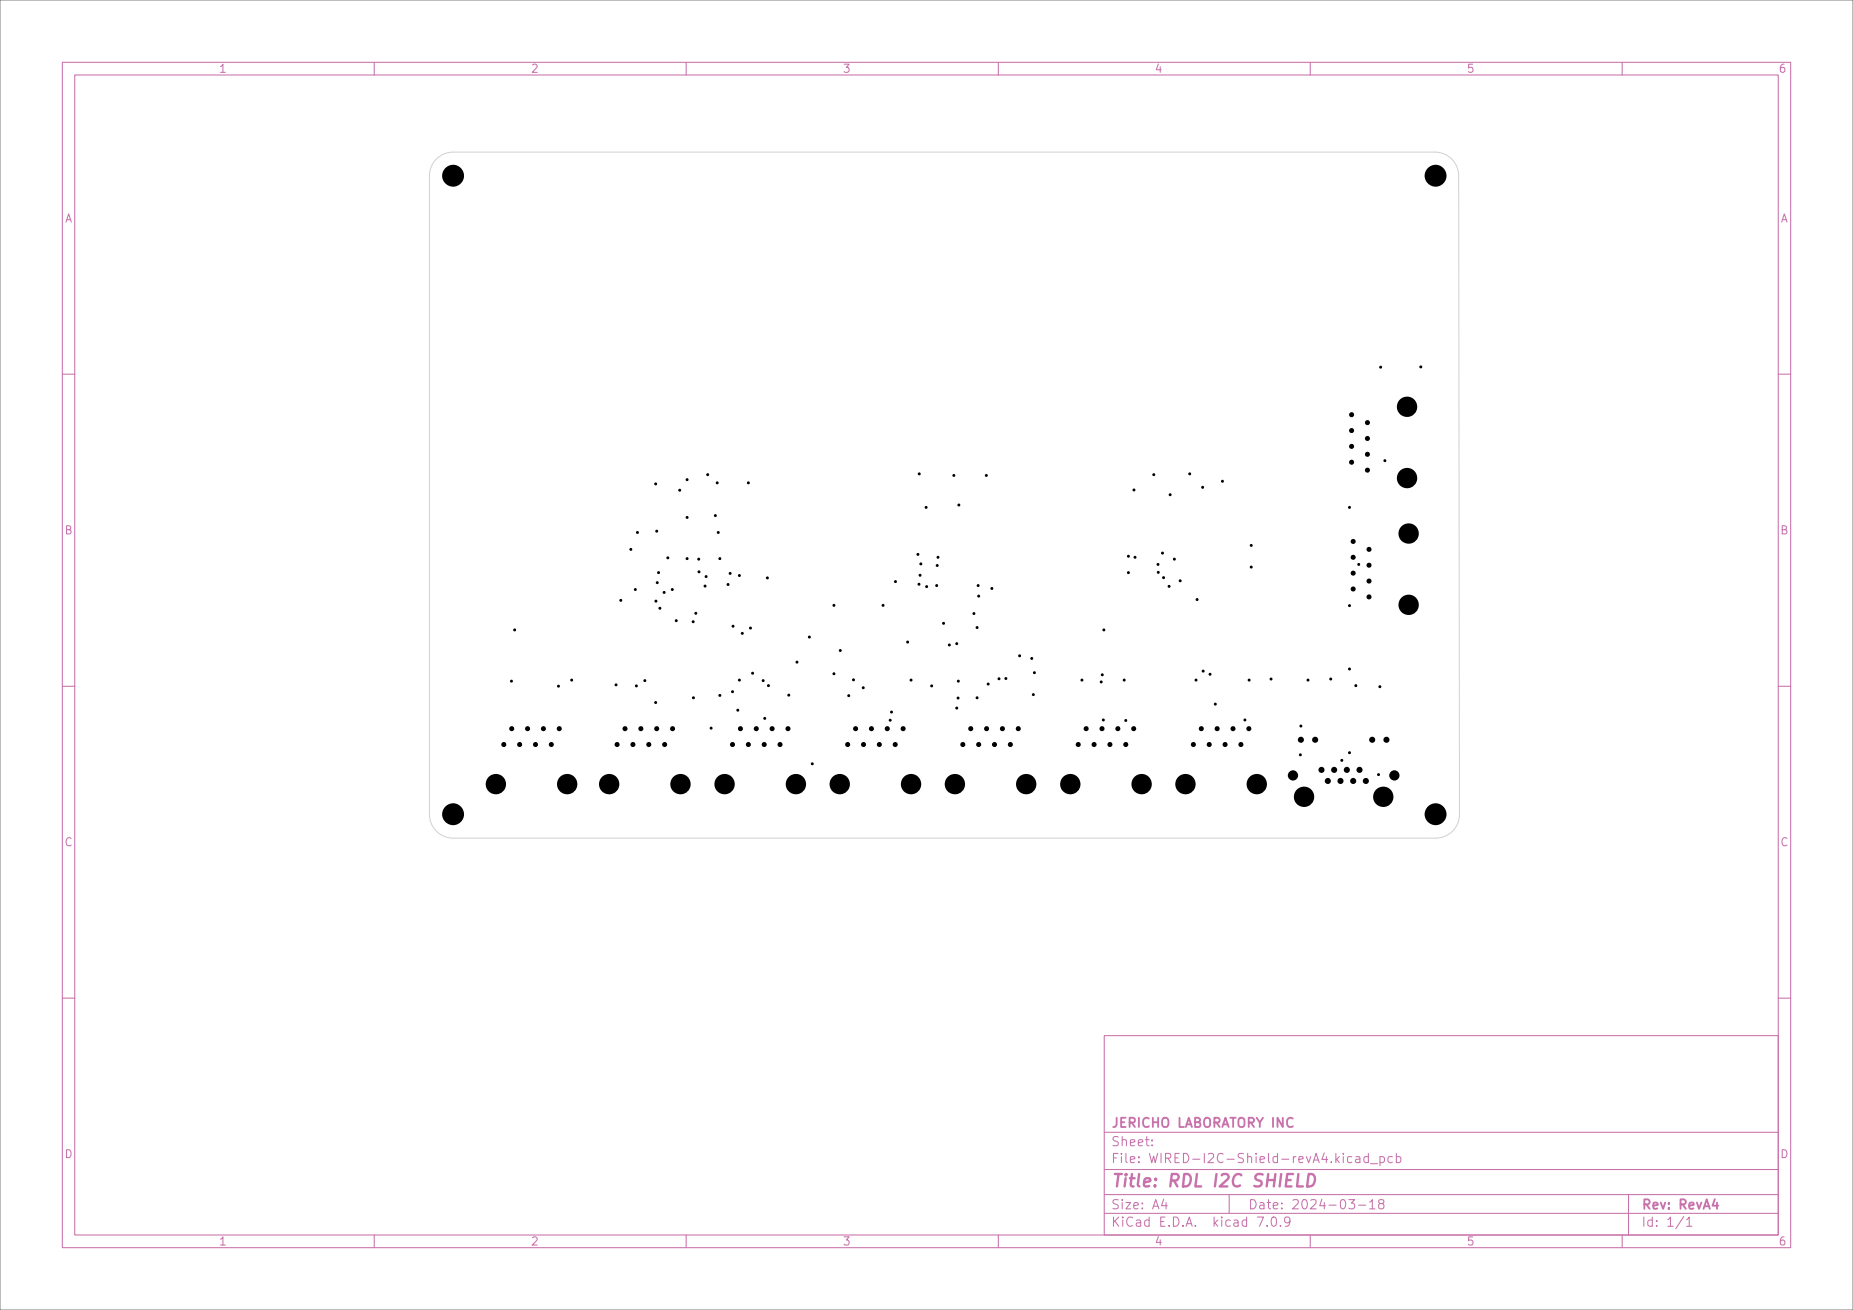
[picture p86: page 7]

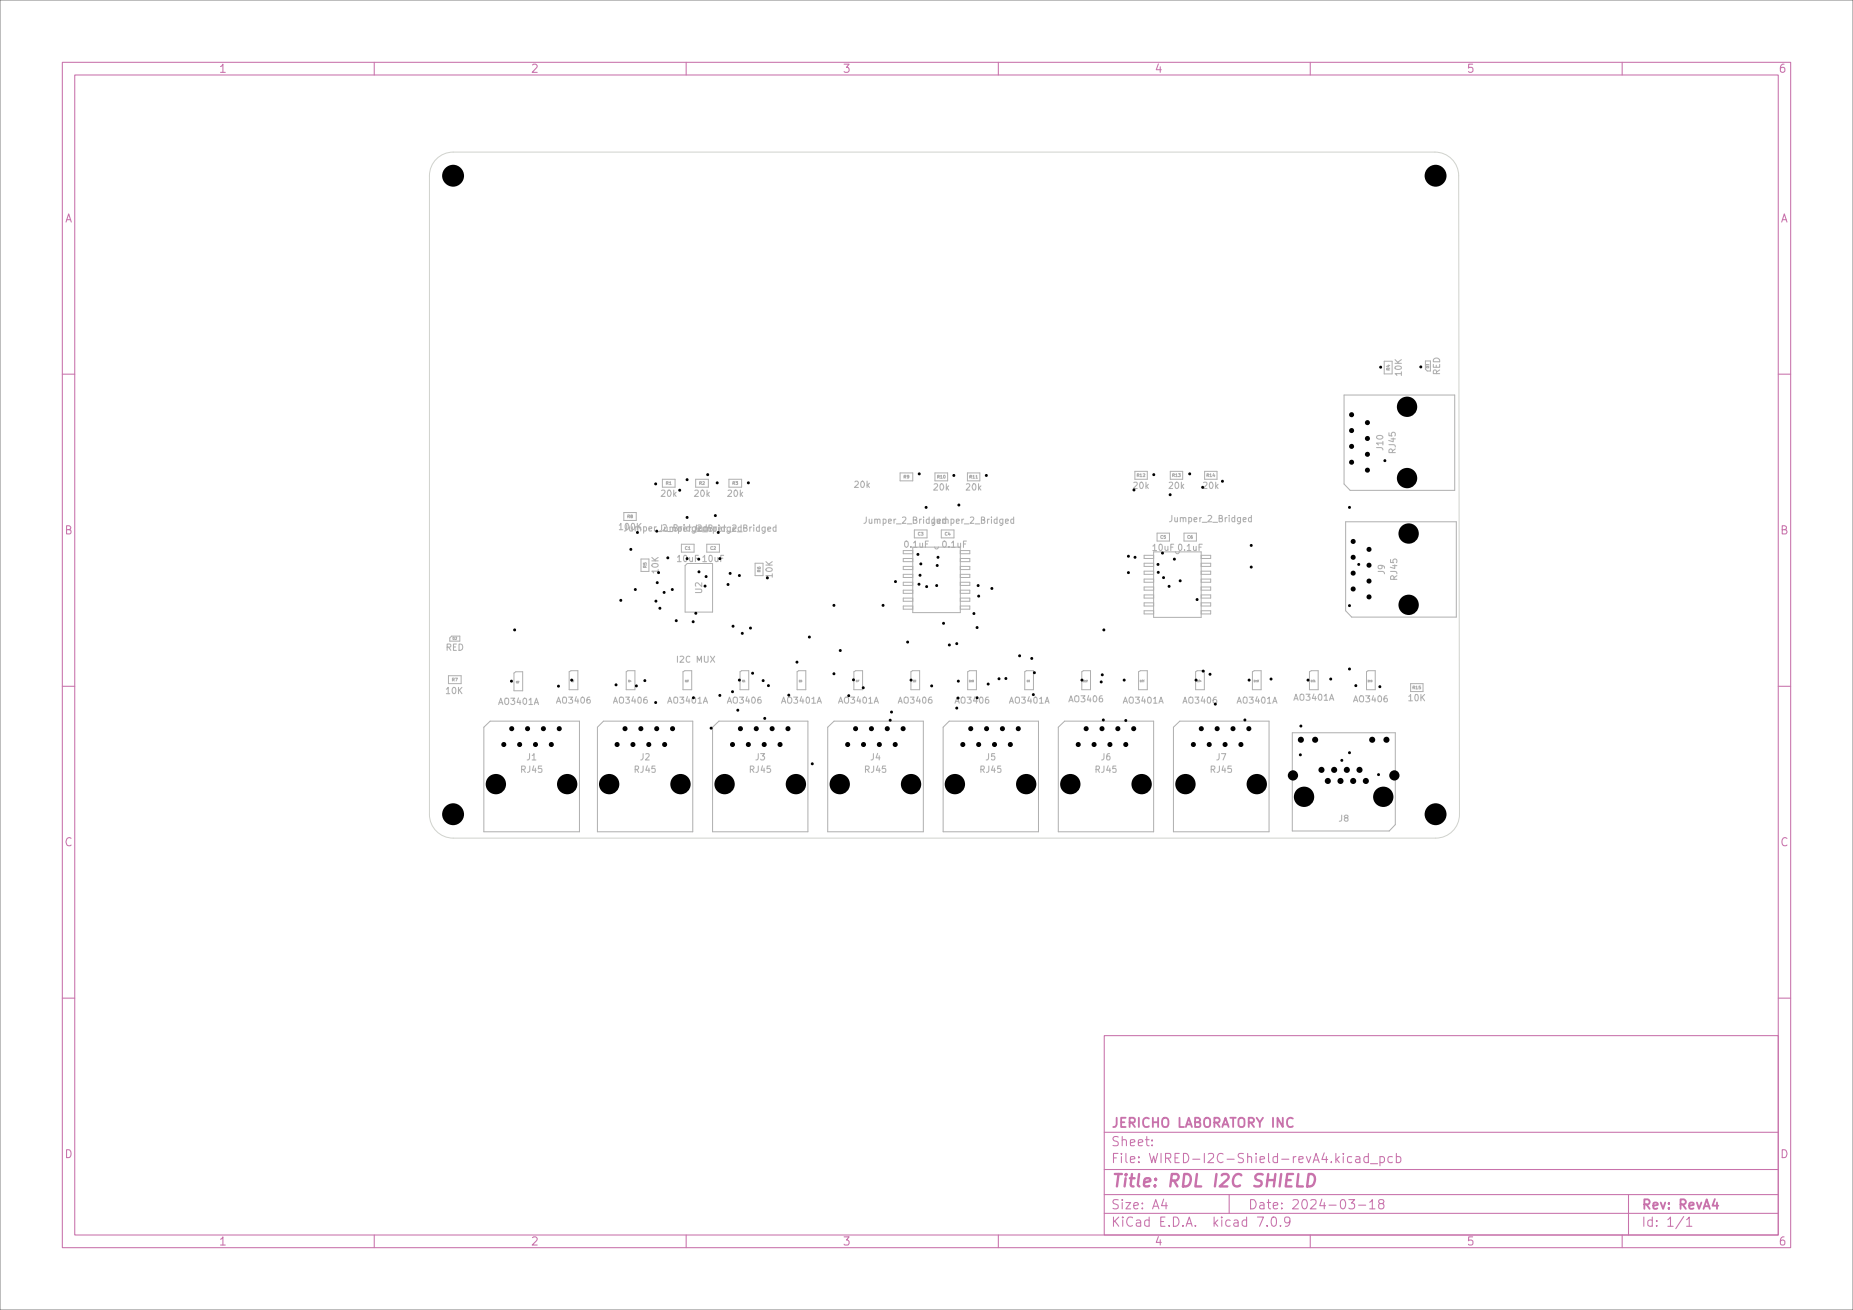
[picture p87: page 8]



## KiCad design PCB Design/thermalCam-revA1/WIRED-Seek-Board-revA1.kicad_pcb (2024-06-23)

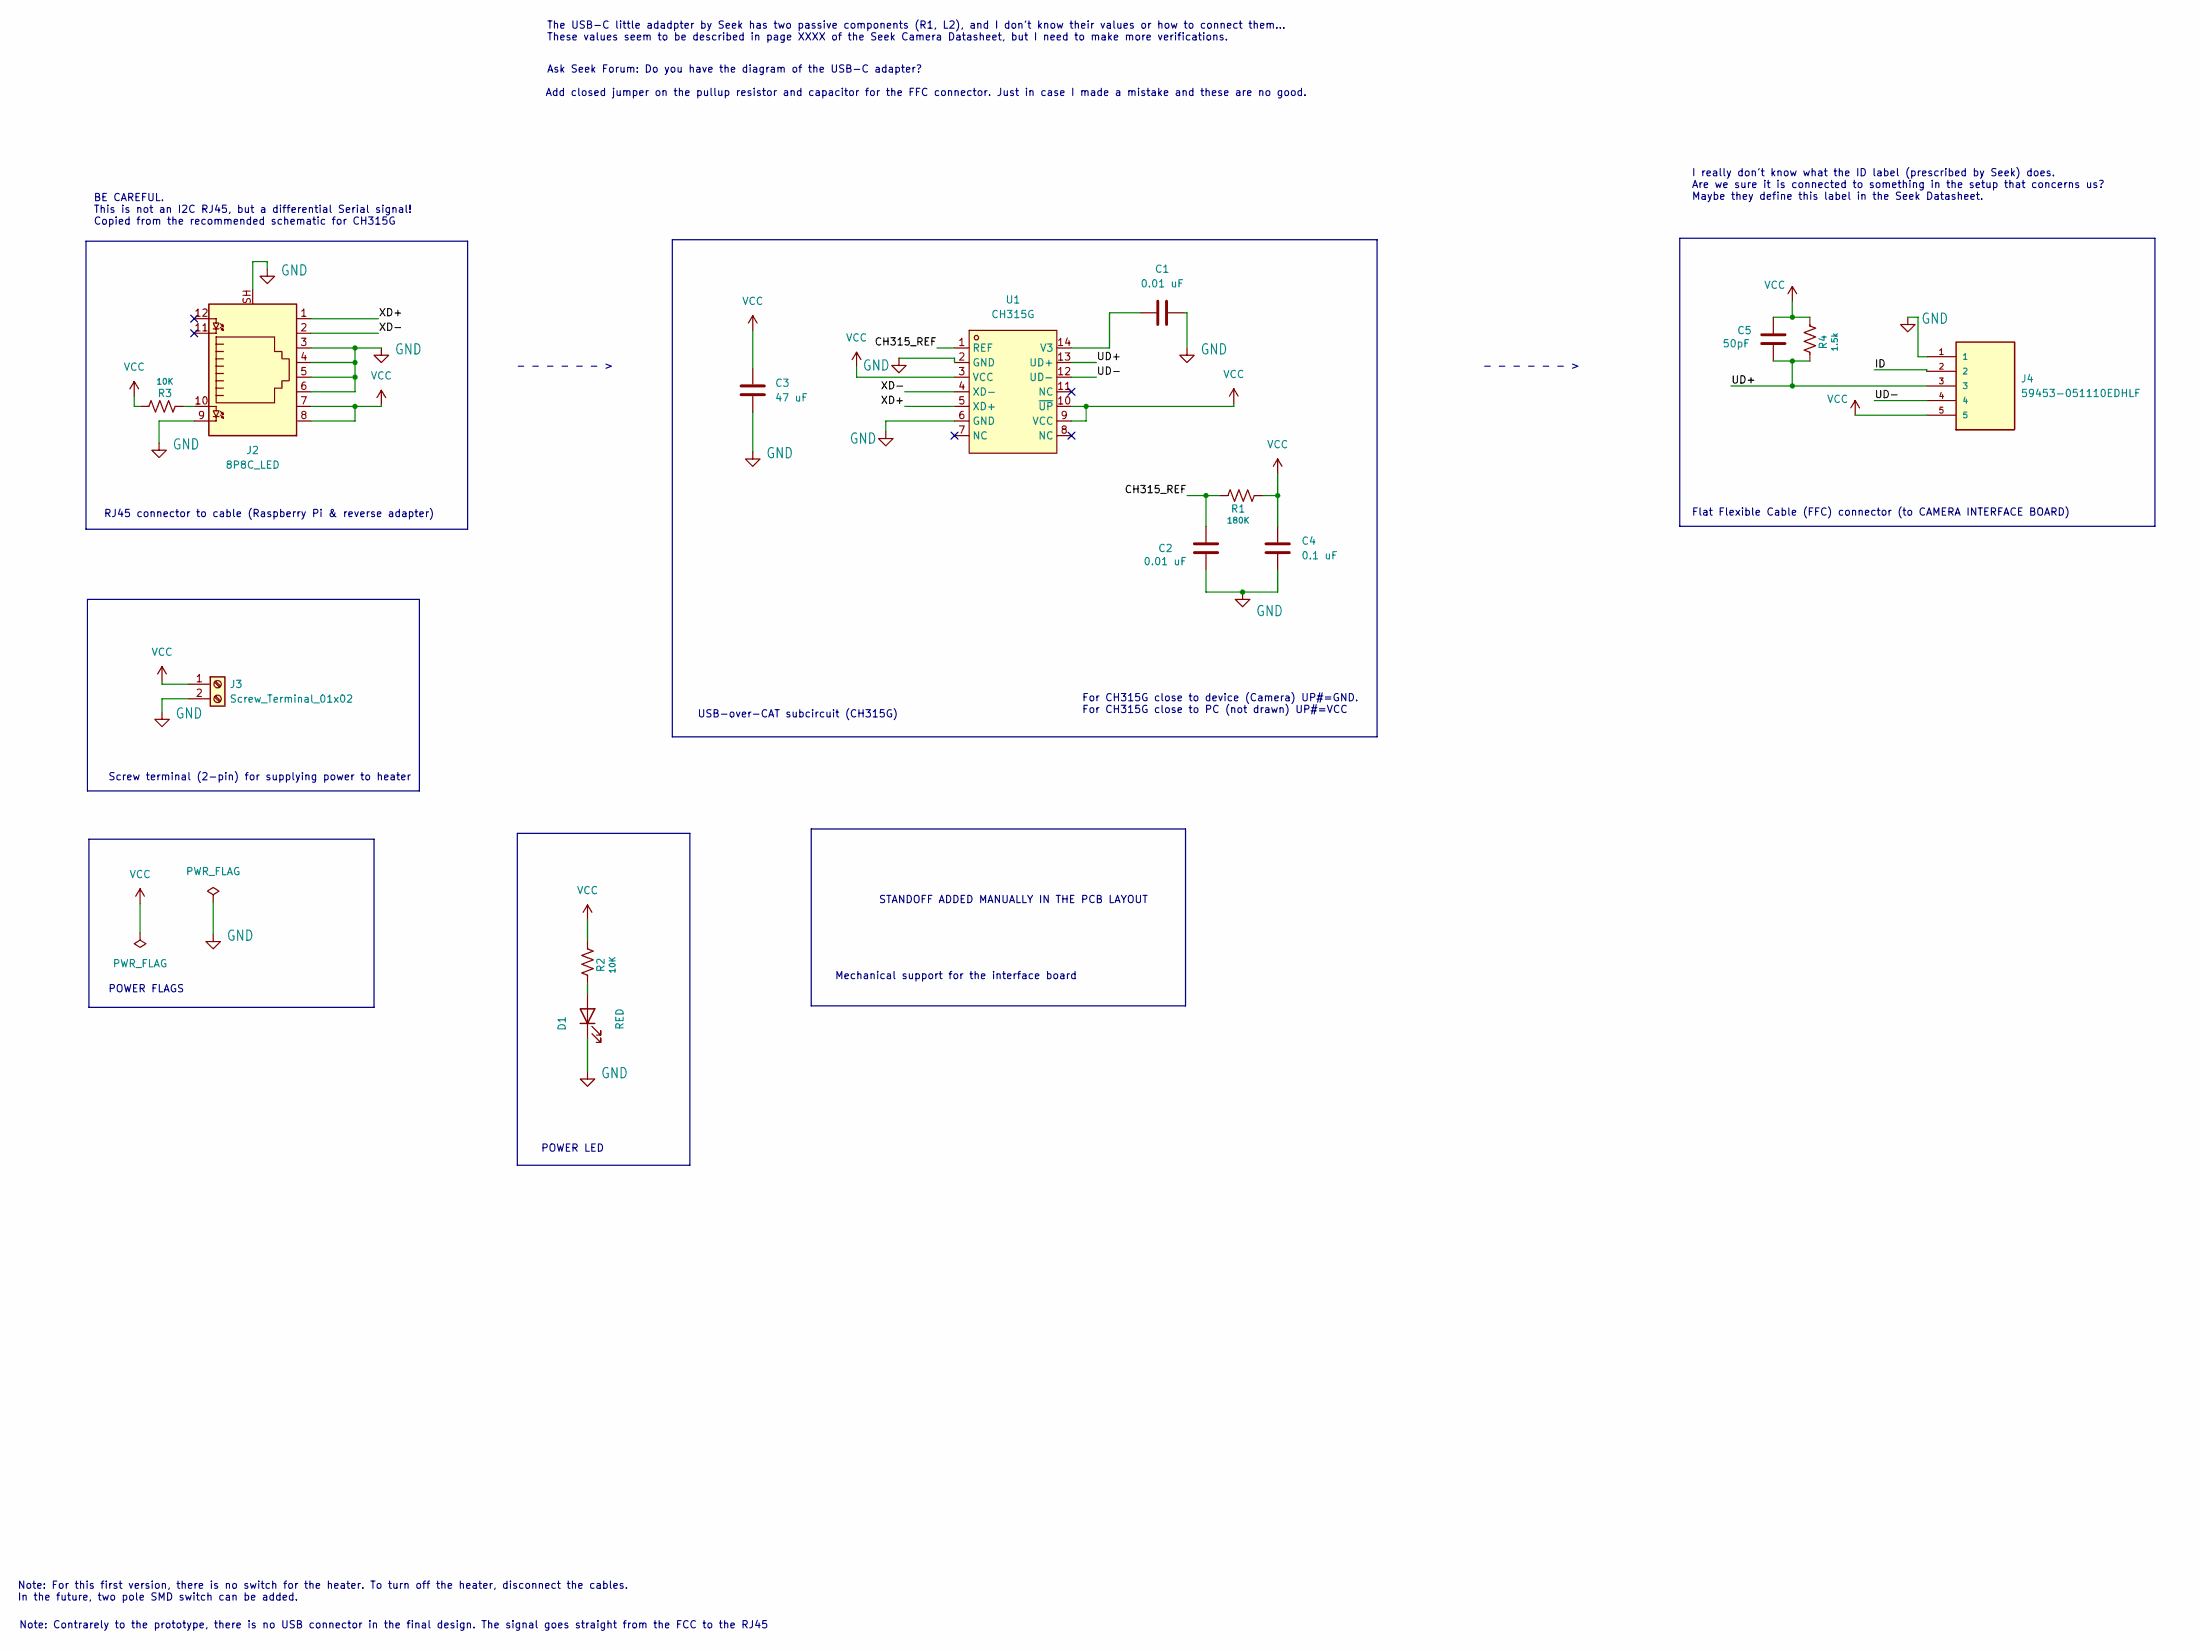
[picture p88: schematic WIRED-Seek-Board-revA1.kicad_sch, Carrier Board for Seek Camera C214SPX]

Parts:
C1, C2: 0.01 uF; C_1206_3216Metric; LCSC C13585
C3: 47 uF; C_1206_3216Metric; LCSC C13585
C4: 0.1 uF; C_1206_3216Metric; LCSC C13585
C5: 50pF; C_1206_3216Metric; LCSC C13585
D1: RED; D_0603_1608Metric; LCSC C2286
J2: 8P8C_LED; RJ45_Amphenol_RJHSE538X; LCSC C386757
J3: Screw_Terminal_01x02; Term_Block_1x2_P5mm
J4: 59453-051110EDHLF; AMPHENOL_59453-051110EDHLF; PARTREV D
R1: 180K; R_0805_2012Metric; LCSC C17713
R2, R3: 10K; R_0805_2012Metric; LCSC C17414
R4: 1.5k; R_0805_2012Metric
U1: CH315G; CH315g-LCSC; LCSC Part C92287

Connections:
/CH315_REF: C2.2, R1.1, U1.1 (REF)
/ID: J4.2
/UD+: C5.1, J4.3, R4.1, U1.13 (UD+)
/UD-: J4.4, U1.12 (UD-)
/XD+: J2.1, U1.5 (XD+)
/XD-: J2.2, U1.4 (XD-)
GND: C1.2, C2.1, C3.2, C4.2, D1.1 (K), J2.3, J2.4, J2.5, J2.6, J2.9, J2.SH, J3.2, J4.1, U1.2 (GND), U1.6 (GND)
unnamed: D1.2 (A), R2.1
unnamed: J2.10, R3.1
unnamed: C1.1, U1.14 (V3)
VCC: C3.1, C4.1, C5.2, J2.7, J2.8, J3.1, J4.5, R1.2, R2.2, R3.2, R4.2, U1.3 (VCC), U1.9 (VCC), U1.10 (~UP)

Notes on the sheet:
I really don't know what the ID label (prescribed by Seek) does. Are we sure it is connected to something in the setup that concerns us? Maybe they define this label in the Seek Datasheet.
STANDOFF ADDED MANUALLY IN THE PCB LAYOUT
The USB-C little adadpter by Seek has two passive components (R1, L2), and I don't know their values or how to connect them... These values seem to be described in page XXXX of the Seek Camera Datasheet, but I need to make more verifications.
POWER LED
- - - - - - >
USB-over-CAT subcircuit (CH315G)
Note: For this first version, there is no switch for the heater. To turn off the heater, disconnect the cables. In the future, two pole SMD switch can be added.
For CH315G close to device (Camera) UP#=GND. For CH315G close to PC (not drawn) UP#=VCC
RJ45 connector to cable (Raspberry Pi & reverse adapter)
Add closed jumper on the pullup resistor and capacitor for the FFC connector. Just in case I made a mistake and these are no good.
Screw terminal (2-pin) for supplying power to heater
Mechanical support for the interface board
Note: Contrarely to the prototype, there is no USB connector in the final design. The signal goes straight from the FCC to the RJ45
POWER FLAGS
Ask Seek Forum: Do you have the diagram of the USB-C adapter?
Flat Flexible Cable (FFC) connector (to CAMERA INTERFACE BOARD)
BE CAREFUL. This is not an I2C RJ45, but a differential Serial signal! Copied from the recommended schematic for CH315G

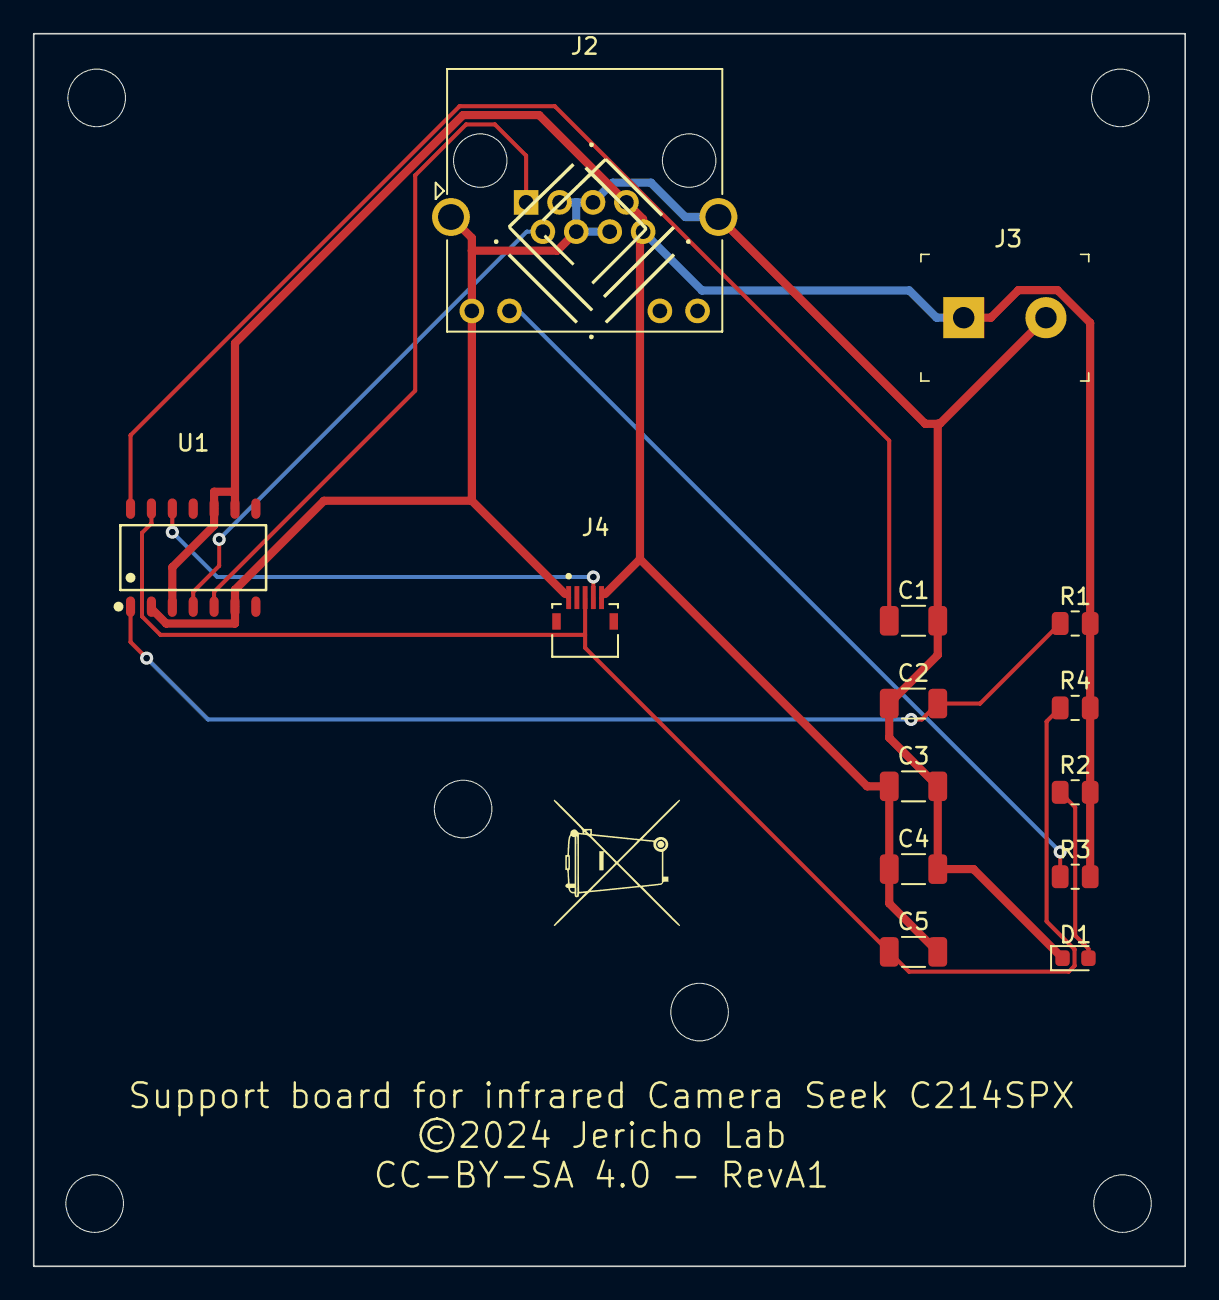
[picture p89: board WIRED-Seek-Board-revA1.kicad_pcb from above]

Board: 2 copper layers, 70.0 x 74.9 mm, 23 parts (1 on the bottom side), 10 nets.

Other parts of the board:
G1: LOGO; jericho-logo-kicad
G2: LOGO; Do not throw to garbage logo WEEE2
G3: LOGO; made-in-canada
H1, H2, H3, H4, H5, H6: MountingHole_3.5mm

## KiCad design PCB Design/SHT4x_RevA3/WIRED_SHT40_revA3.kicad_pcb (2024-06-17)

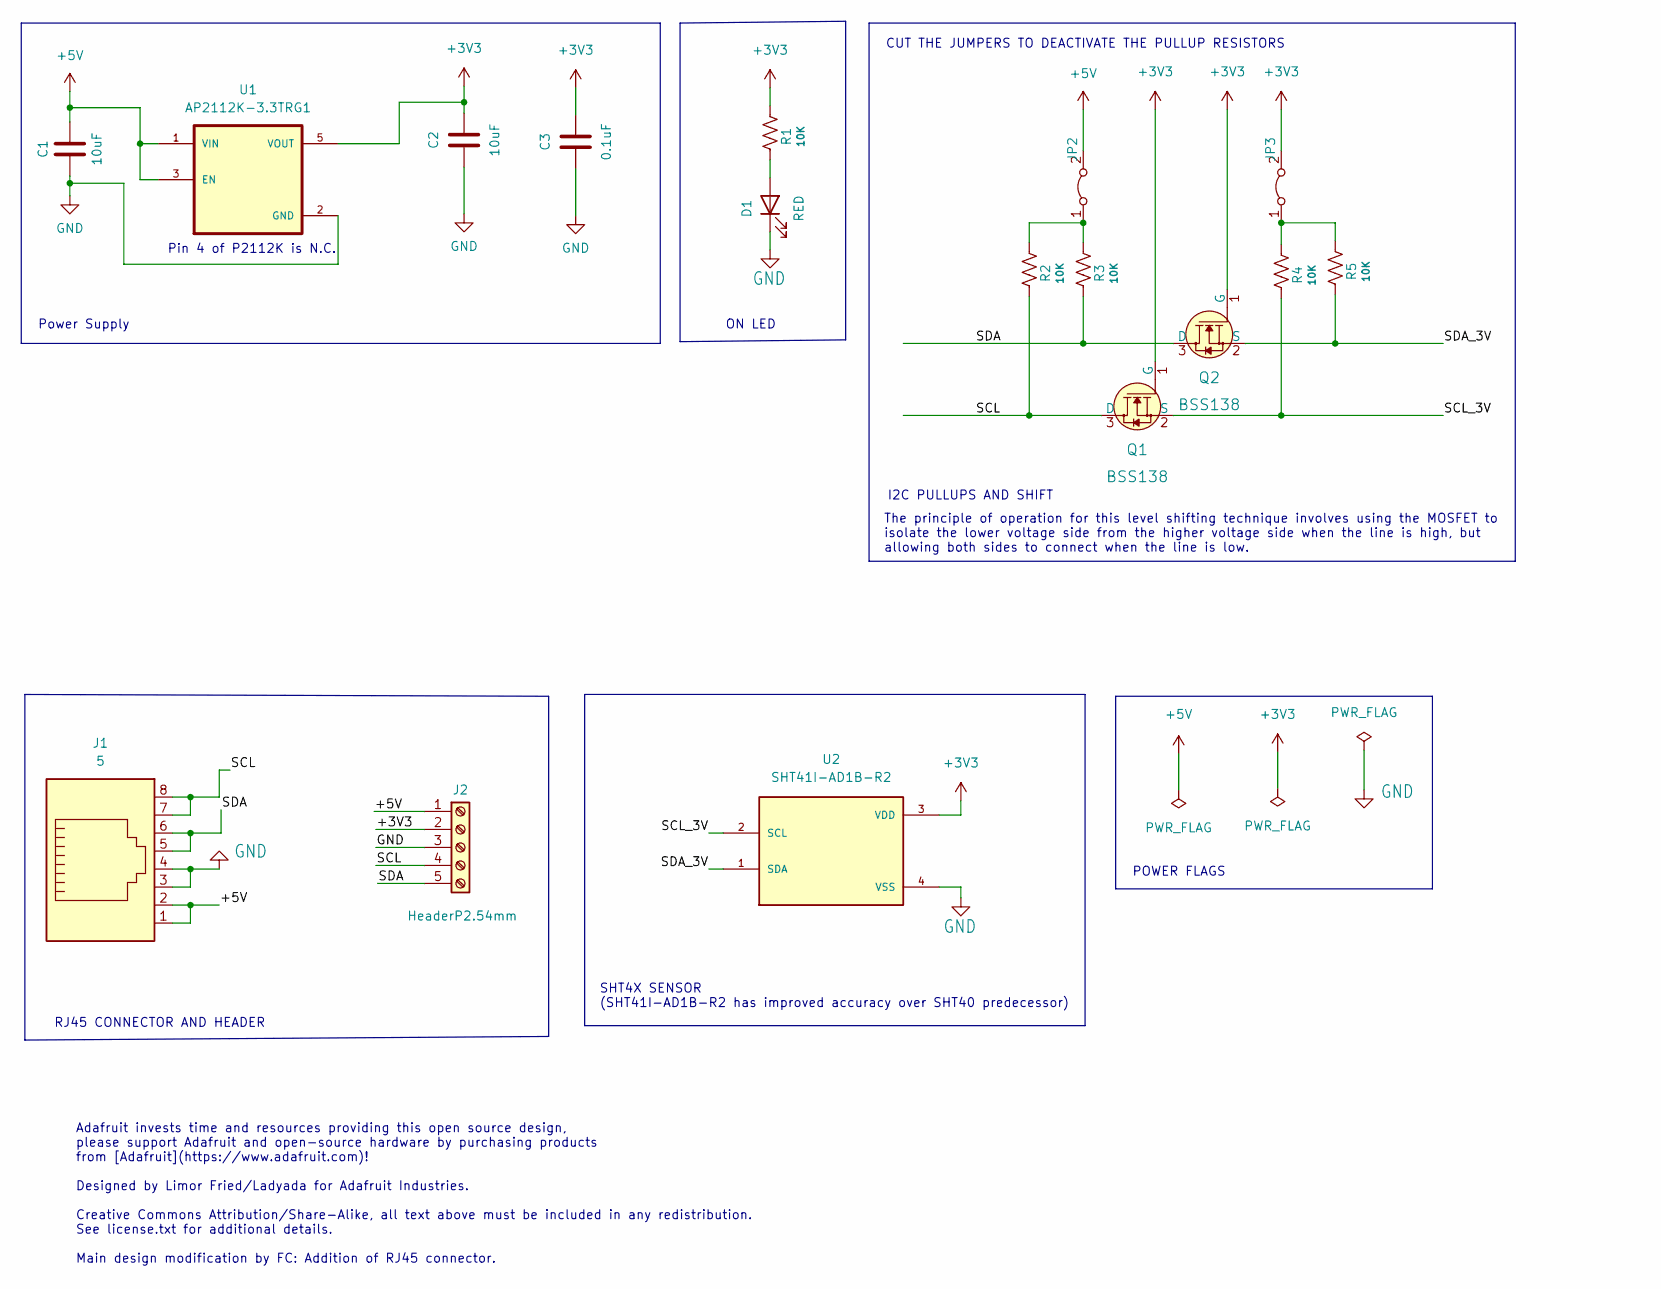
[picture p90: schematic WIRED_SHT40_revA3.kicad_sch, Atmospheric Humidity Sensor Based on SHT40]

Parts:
C1, C2: 10uF; C_0805_2012Metric; LCSC C440198
C3: 0.1uF; C_0805_2012Metric; LCSC C49678
D1: RED; D_0603_1608Metric; LCSC C2286
J1: 5; RJ45_Amphenol_54602-x08_Horizontal; LCSC C3000197
J2: HeaderP2.54mm; PinHeader_1x05_P2.54mm_Vertical; LCSC C706877
JP2, JP3: Jumper_2_Bridged; SolderJumper-2_P1.3mm_Bridged_Pad1.0x1.5mm
Q1, Q2: BSS138; SOT-23-3; MPN BSS138; Digi-Key_PN BSS138CT-ND
R1, R2, R3, R4, R5: 10K; R_0805_2012Metric; LCSC C17414
U1: AP2112K-3.3TRG1; SOT95P285X140-5N; PARTREV 2-2; LCSC C51118
U2: SHT41I-AD1B-R2; SHT4X; LCSC C3664410

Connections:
+3V3: C2.1, C3.1, J2.2, JP3.2 (B), Q1.1 (G), Q2.1 (G), R1.2, U1.5 (VOUT), U2.3 (VDD)
+5V: C1.1, J1.1, J1.2, J2.1, JP2.2 (B), U1.1 (VIN), U1.3 (EN)
/SCL: J1.7, J1.8, J2.4, Q1.3 (D), R2.1
/SCL_3V: Q1.2 (S), R4.1, U2.2 (SCL)
/SDA: J1.5, J1.6, J2.5, Q2.3 (D), R3.1
/SDA_3V: Q2.2 (S), R5.1, U2.1 (SDA)
GND: C1.2, C2.2, C3.2, D1.1 (K), J1.3, J1.4, J2.3, U1.2 (GND), U2.4 (VSS)
unnamed: D1.2 (A), R1.1
unnamed: JP2.1 (A), R2.2, R3.2
unnamed: JP3.1 (A), R4.2, R5.2

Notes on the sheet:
SHT4X SENSOR (SHT41I-AD1B-R2 has improved accuracy over SHT40 predecessor)
Power Supply
ON LED
Adafruit invests time and resources providing this open source design, please support Adafruit and open-source hardware by purchasing products from [Adafruit](https://www.adafruit.com)! Designed by Limor Fried/Ladyada for Adafruit Industries. Creative Commons Attribution/Share-Alike, all text above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
Pin 4 of P2112K is N.C.
POWER FLAGS
RJ45 CONNECTOR AND HEADER
The principle of operation for this level shifting technique involves using the MOSFET to isolate the lower voltage side from the higher voltage side when the line is high, but allowing both sides to connect when the line is low.
I2C PULLUPS AND SHIFT
CUT THE JUMPERS TO DEACTIVATE THE PULLUP RESISTORS

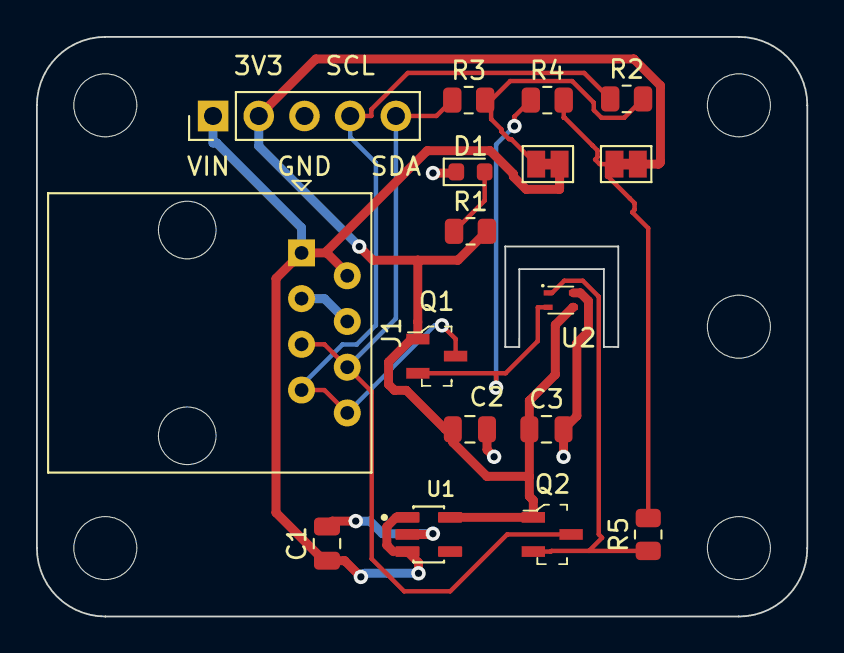
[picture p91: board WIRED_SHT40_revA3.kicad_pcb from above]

Board: 2 copper layers, 42.8 x 32.2 mm, 23 parts (1 on the bottom side), 10 nets.

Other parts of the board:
G1: LOGO; Do not throw to garbage logo WEEE2
H1, H2, H3, H4, H5: MountingHole_3.5mm

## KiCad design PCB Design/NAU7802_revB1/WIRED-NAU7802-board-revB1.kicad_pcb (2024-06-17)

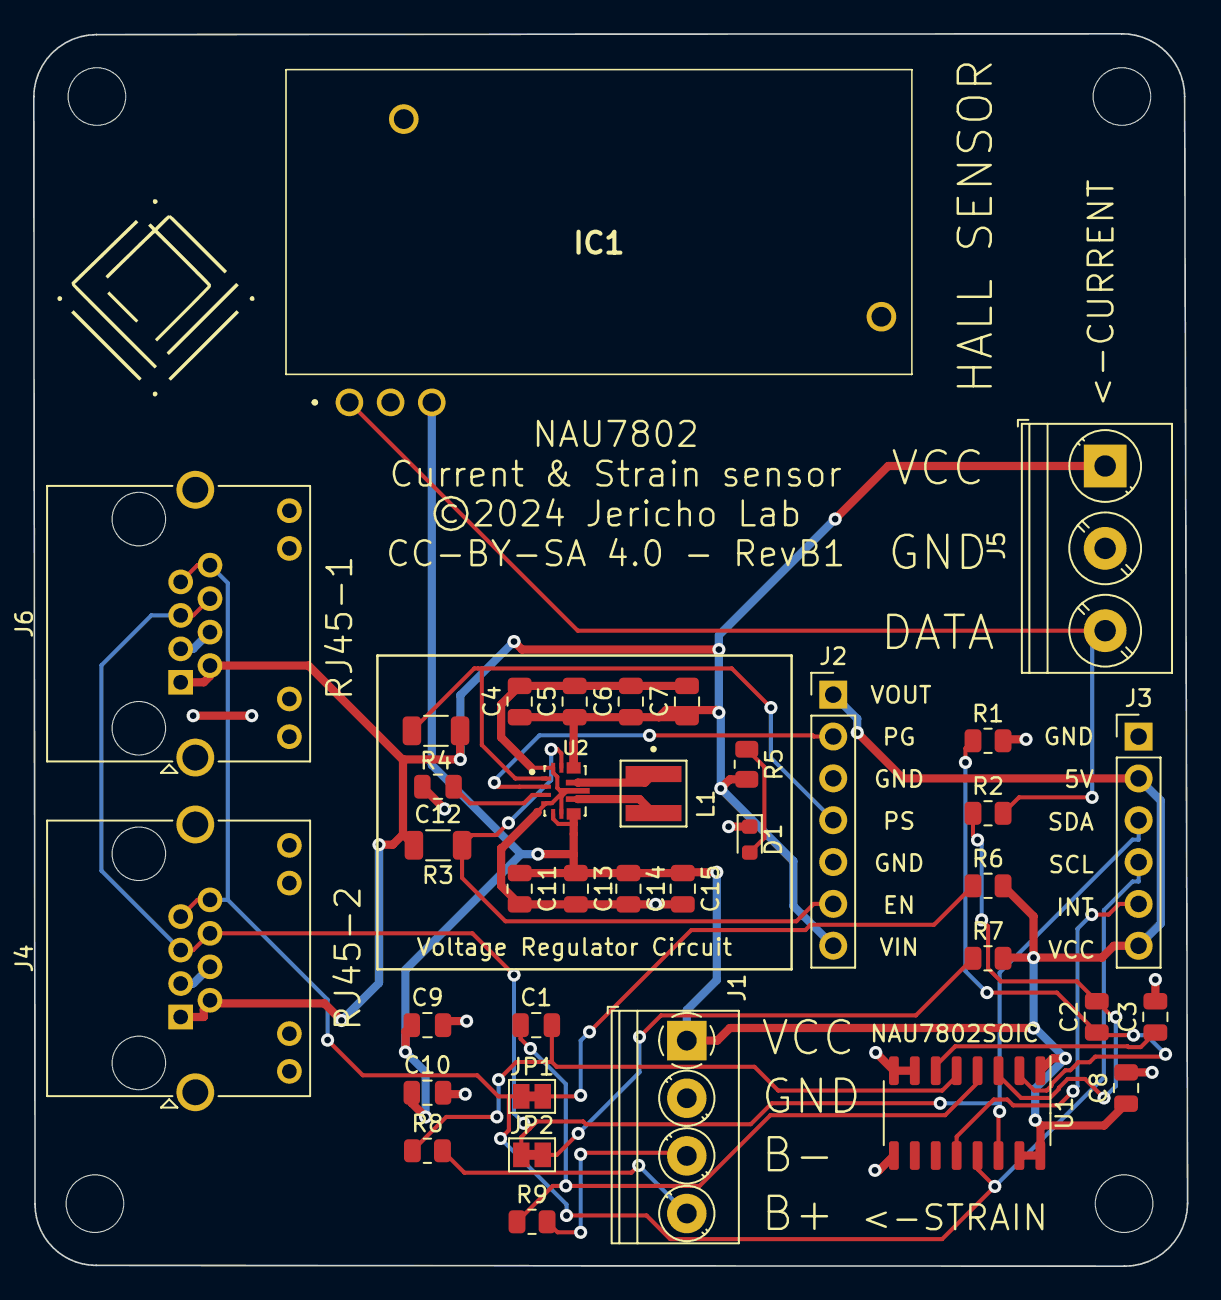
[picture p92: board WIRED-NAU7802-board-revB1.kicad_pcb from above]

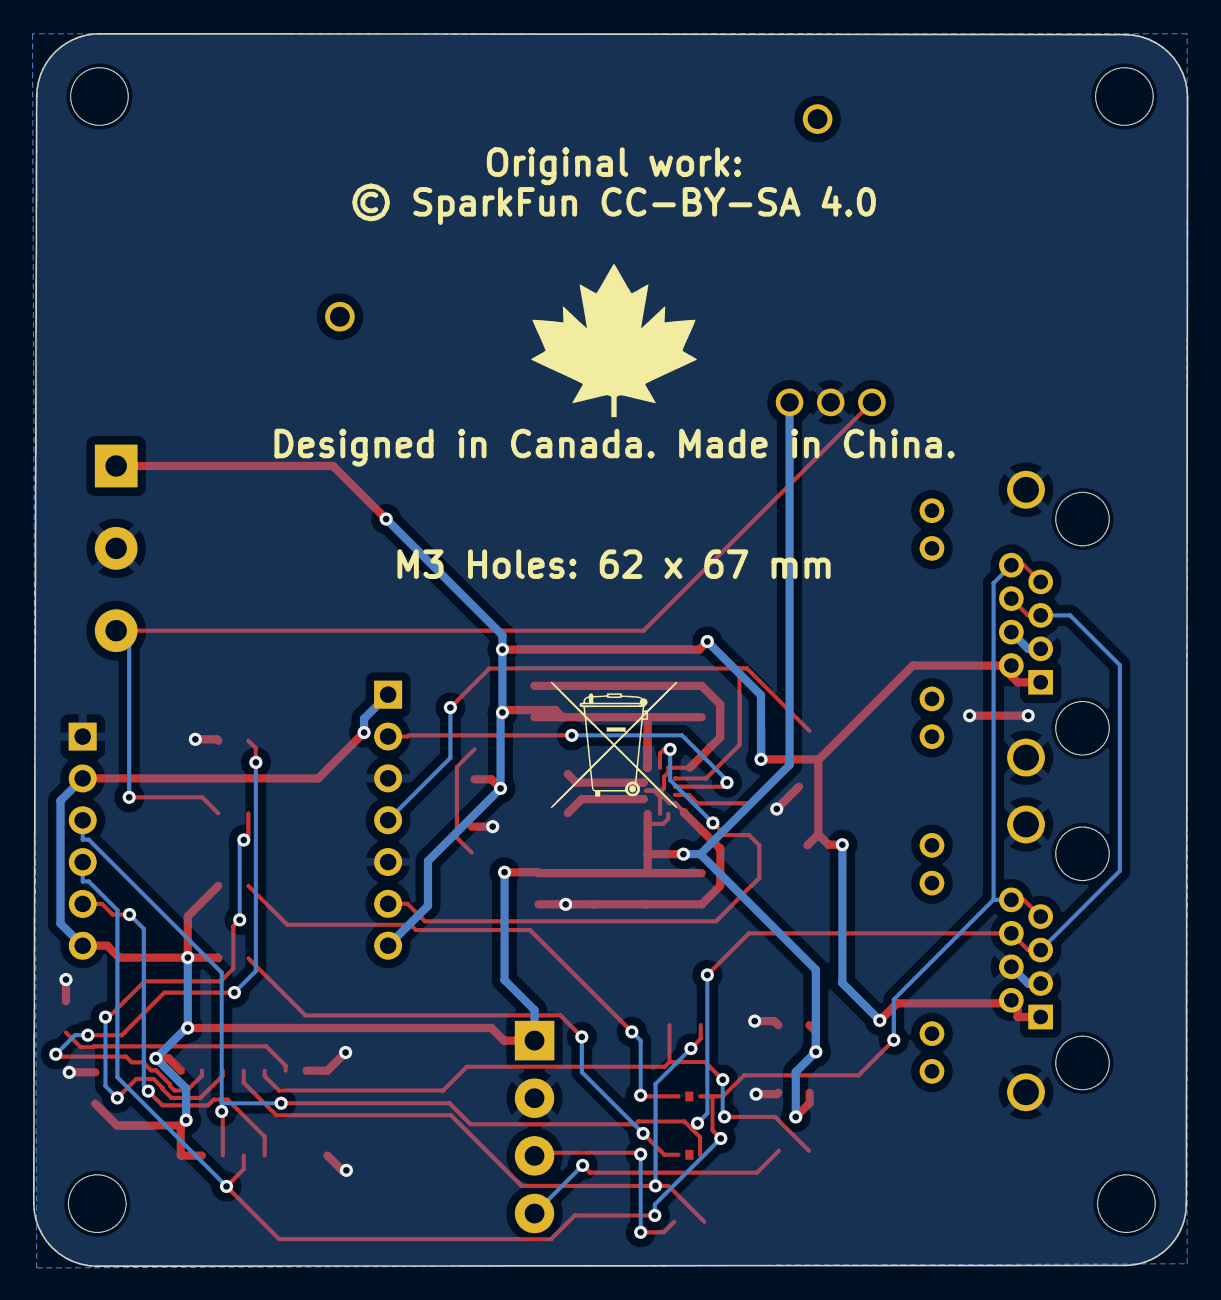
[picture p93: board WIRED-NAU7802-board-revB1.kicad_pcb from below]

Board: 2 copper layers, 70.1 x 74.8 mm, 44 parts (2 on the bottom side), 23 nets.

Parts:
C1, C2, C3, C4, C10, C12: 0.1uF; C_0805_2012Metric
C5, C6, C7, C9, C11: 10uF; C_0805_2012Metric
C8, C13, C14, C15: 22uF; C_0805_2012Metric
D1: RED; D_0603_1608Metric
G1: LOGO; jericho-logo-kicad
G2: LOGO; made-in-canada
G3: LOGO; Do not throw to garbage logo WEEE2
H1, H2, H3, H4: MountingHole_3.5mm
IC1: L01Z050S05
J1: TerminalBlock_Phoenix_PT-1,5-4-3.5-H_1x04_P3.50mm_Horizontal
J2: HeaderP2.54mm; PinHeader_1x07_P2.54mm_Vertical
J3: HeaderP2.54mm; PinHeader_1x06_P2.54mm_Vertical
J4, J6: 8P8C_LED_Shielded; RJ45_Amphenol_RJHSE538X
J5: Screw_Terminal_01x03; TerminalBlock_Phoenix_PT-1,5-3-5.0-H_1x03_P5.00mm_Horizontal
JP1, JP2: Jumper_2_Bridged; SolderJumper-2_P1.3mm_Bridged_Pad1.0x1.5mm
L1: 1.5uH; IND_XFL4020-152MEC
R1, R2, R8, R9: 47; R_0805_2012Metric
R3, R4: 10k; R_1206_3216Metric
R5: 10K; R_0805_2012Metric
R6, R7: 2.2K; R_0805_2012Metric
U1: NAU7802SOIC; SO-16_3.9x9.9mm_P1.27mm
U2: TPS630701RNMR; VREG_TPS63070RNMR

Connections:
+5V: C4.1, C5.1, C6.1, C7.1, J2.7, J4.1, J4.2, J5.1, J6.1, J6.2, R3.2, R4.1, R5.2, U2.12_13 (VIN)
/B+: J1.4, R8.2
/B-: J1.3, R9.2
/DATA: IC1.1 (VOUT), J5.3, R2.2
/INT: J3.5, U1.12 (DRDY)
/SCL: J3.4, J4.7, J4.8, J6.7, J6.8, JP1.1 (A), U1.13 (SCLK)
/SDA: J3.3, J4.5, J4.6, J6.5, J6.6, JP2.1 (A), U1.14 (SDIO)
EN: J2.6, R3.1, U2.14 (EN)
GND: C3.2, C4.2, C5.2, C6.2, C7.2, C8.2, C9.2, C10.2, C11.2, C12.2, C13.2, C14.2, C15.2, D1.1 (K), IC1.2 (GND), J1.2, J2.3, J2.5, J3.1, J4.3, J4.4, J4.SH, J5.2, J6.3, J6.4, J6.SH, R1.2, U1.7 (REFN), U1.8 (AVSS), U1.9 (DVSS), U2.4 (GND), U2.6 (FB2), U2.10 (PGND), U2.15 (VSEL)
unnamed: D1.2 (A), R5.1
unnamed: JP1.2 (B), R6.1
unnamed: JP2.2 (B), R7.1
unnamed: C3.1, U1.6 (VBG)
unnamed: C2.1, R1.1, U1.2 (VIN1N)
unnamed: C2.2, R2.1, U1.3 (VIN1P)
unnamed: C1.1, R9.1, U1.4 (VIN2N)
unnamed: C1.2, R8.1, U1.5 (VIN2P)
unnamed: L1.1, U2.11 (L1)
unnamed: L1.2, U2.9 (L2)
unnamed: C12.1, U2.3 (VAUX)
PG: J2.2, U2.2 (PG)
PS: J2.4, R4.2, U2.1 (PS/SYNC)
VCC: C8.1, C9.1, C10.1, C11.1, C13.1, C14.1, C15.1, IC1.3 (+VCC_(+5V)), J1.1, J2.1, J3.2, J3.6, R6.2, R7.2, U1.1 (REFP), U1.15 (DVDD), U1.16 (AVDD), U2.5 (FB), U2.7_8 (VOUT)

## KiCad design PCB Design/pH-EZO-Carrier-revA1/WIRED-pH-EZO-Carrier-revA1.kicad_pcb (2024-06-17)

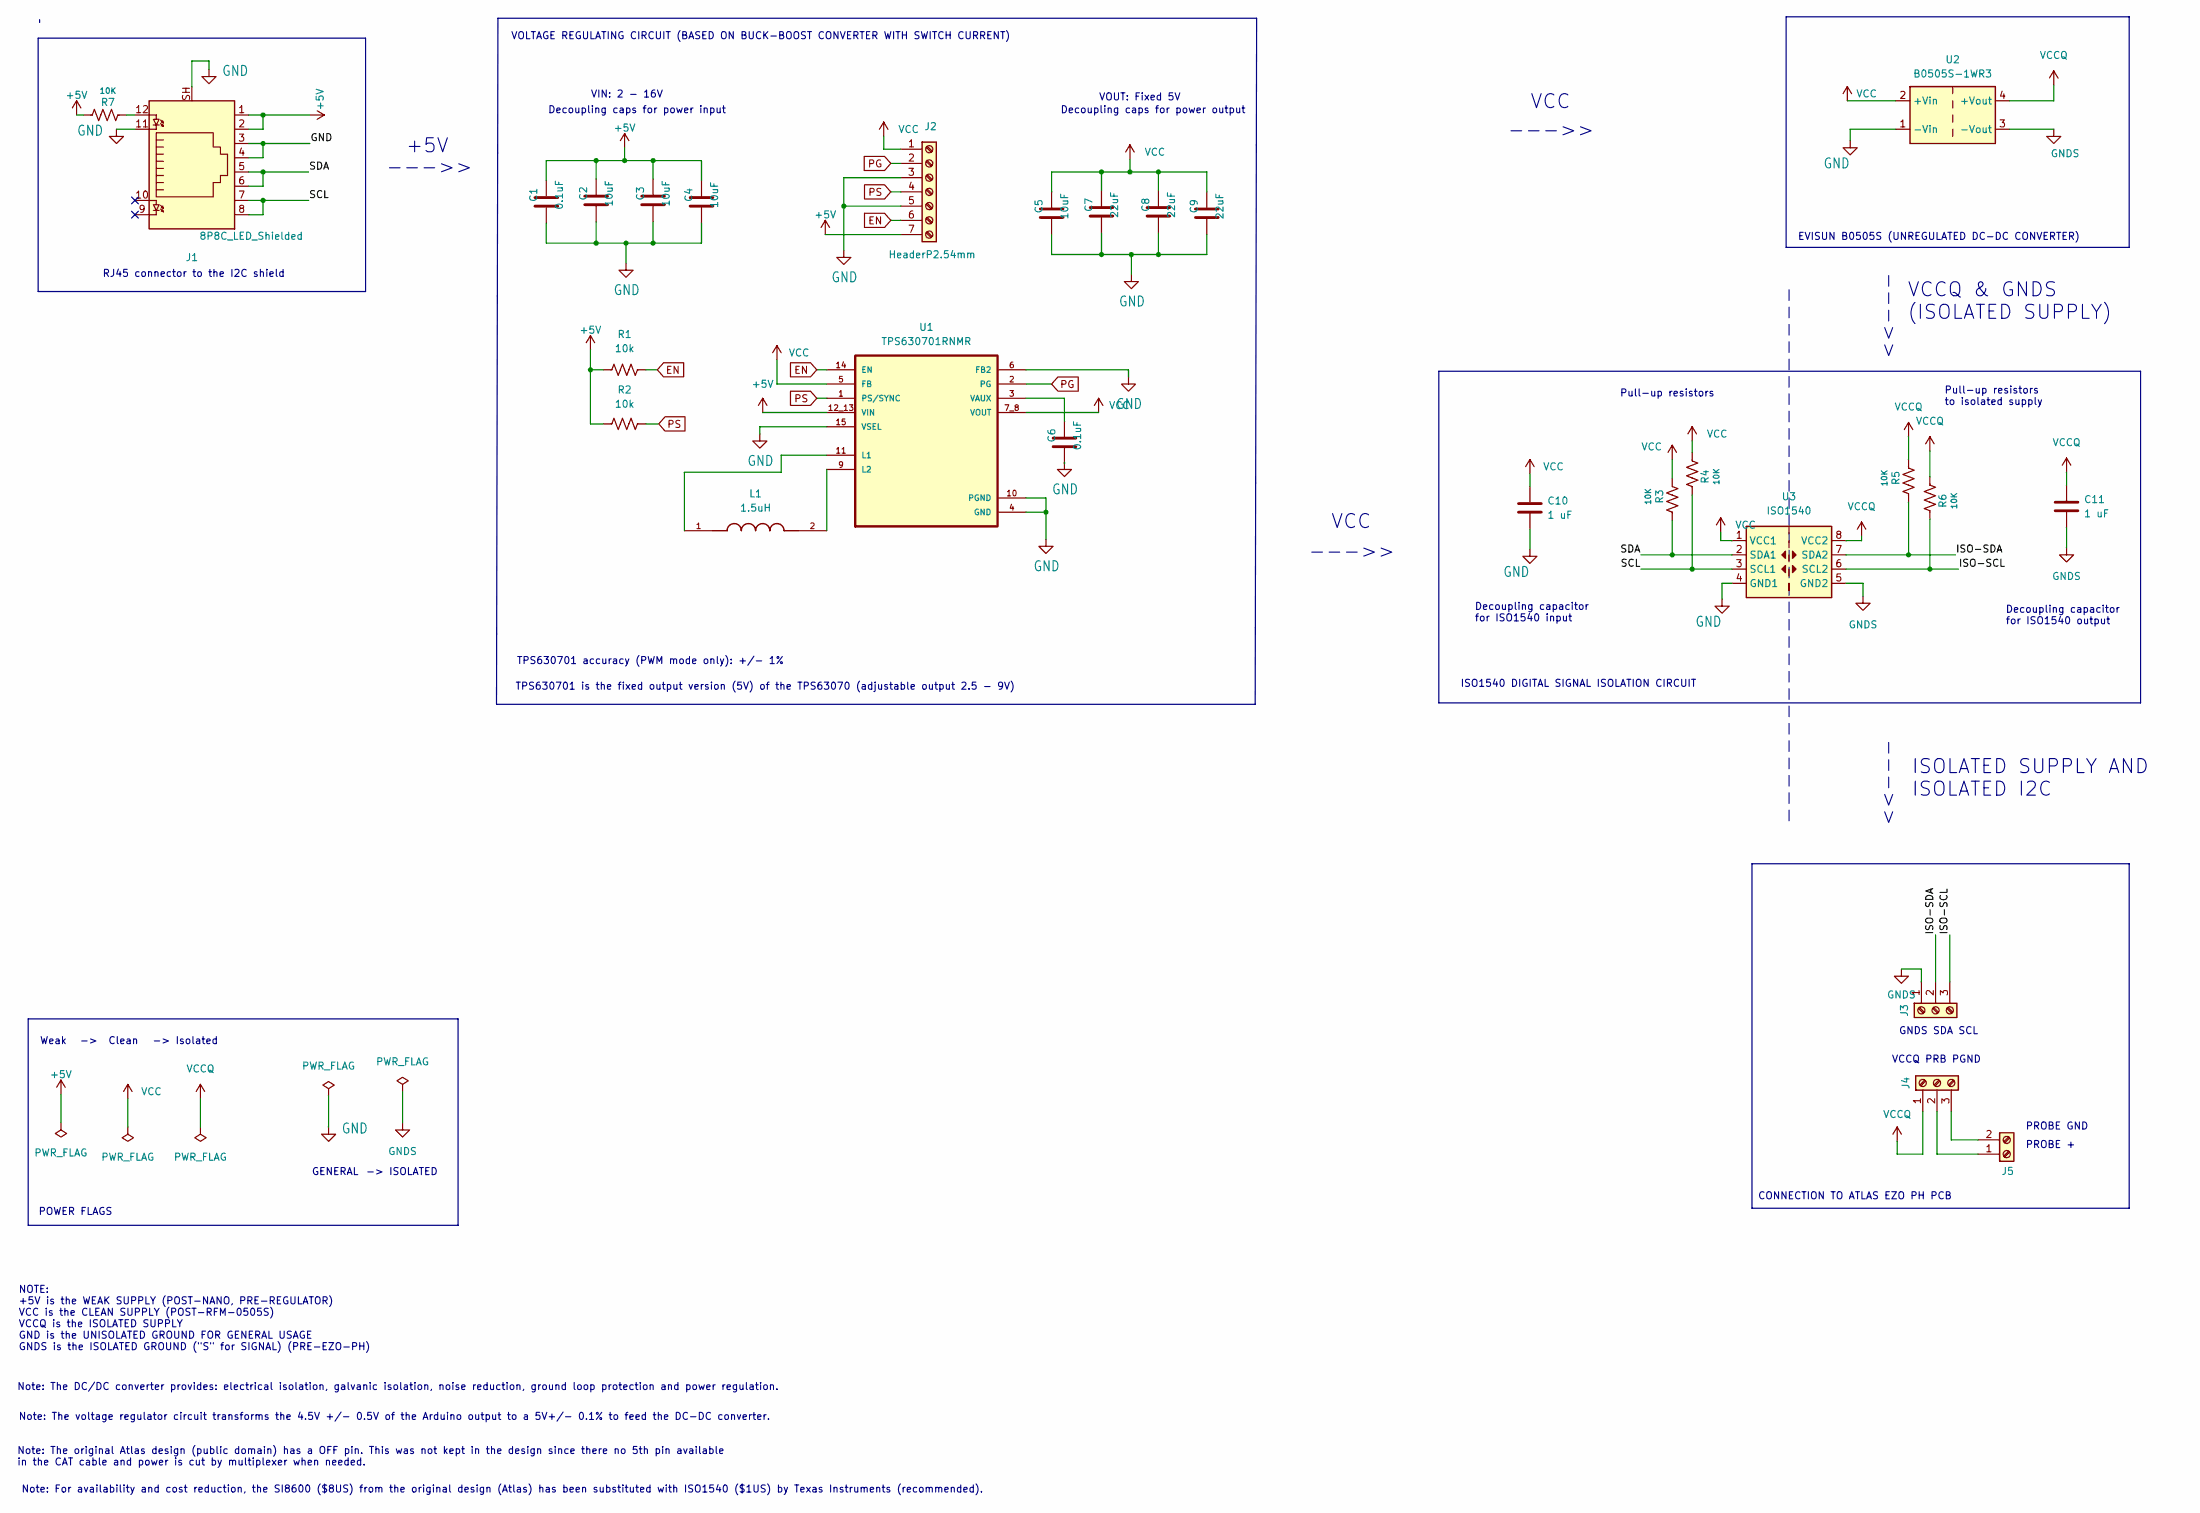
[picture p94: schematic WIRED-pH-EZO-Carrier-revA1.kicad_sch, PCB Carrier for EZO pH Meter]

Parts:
C1, C6: 0.1uF; C_0805_2012Metric; LCSC C49678
C2, C3, C4, C5: 10uF; C_0805_2012Metric; LCSC C15850
C7, C8, C9: 22uF; C_0805_2012Metric; LCSC C45783
C10, C11: 1 uF; C_1206_3216Metric; LCSC C1848
J1: 8P8C_LED_Shielded; RJ45_Amphenol_RJHSE538X; LCSC C386757
J2: HeaderP2.54mm; PinHeader_1x07_P2.54mm_Vertical; LCSC C492406
J3, J4: HeaderP2.54mm; PinHeader_1x03_P2.54mm_Vertical; LCSC C2897366
J5: Screw_Terminal_01x02; Term_Block_1x2_P5mm; LCSC C557646
L1: 1.5uH; IND_XFL4020-152MEC; PARTREV 11/02/18; LCSC C167802
R1, R2: 10k; R_1206_3216Metric; LCSC C17902
R3, R4, R5, R6, R7: 10K; R_0805_2012Metric; LCSC C17414
U1: TPS630701RNMR; VREG_TPS63070RNMR; LCSC C2876599
U2: B0505S-1WR3; Converter_DCDC_TRACO_TEA1-xxxx_THT; LCSC C7465178
U3: ISO1540; SOIC-8_3.9x4.9mm_P1.27mm; LCSC C179739

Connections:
+5V: C1.1, C2.1, C3.1, C4.1, J1.1, J1.2, J2.7, R1.2, R2.1, R7.2, U1.12_13 (VIN)
/ISO-SCL: J3.3, R6.1, U3.6 (SCL2)
/ISO-SDA: J3.2, R5.2, U3.7 (SDA2)
/SCL: J1.7, J1.8, R4.1, U3.3 (SCL1)
/SDA: J1.5, J1.6, R3.2, U3.2 (SDA1)
EN: J2.6, R1.1, U1.14 (EN)
GND: C1.2, C2.2, C3.2, C4.2, C5.2, C6.2, C7.2, C8.2, C9.2, C10.2, J1.3, J1.4, J1.11, J1.SH, J2.3, J2.5, U1.4 (GND), U1.6 (FB2), U1.10 (PGND), U1.15 (VSEL), U2.1 (-Vin), U3.4 (GND1)
GNDS: C11.2, J3.1, U2.3 (-Vout), U3.5 (GND2)
unnamed: J1.12, R7.1
unnamed: J4.2, J5.1
unnamed: J4.3, J5.2
unnamed: L1.1, U1.11 (L1)
unnamed: L1.2, U1.9 (L2)
unnamed: C6.1, U1.3 (VAUX)
PG: J2.2, U1.2 (PG)
PS: J2.4, R2.2, U1.1 (PS/SYNC)
VCC: C5.1, C7.1, C8.1, C9.1, C10.1, J2.1, R3.1, R4.2, U1.5 (FB), U1.7_8 (VOUT), U2.2 (+Vin), U3.1 (VCC1)
VCCQ: C11.1, J4.1, R5.1, R6.2, U2.4 (+Vout), U3.8 (VCC2)

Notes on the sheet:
Note: The DC/DC converter provides: electrical isolation, galvanic isolation, noise reduction, ground loop protection and power regulation.
Decoupling capacitor for ISO1540 output
GNDS SDA SCL
Decoupling caps for power output
--->>
-> Clean
-> Isolated
VCCQ PRB PGND
TPS630701 is the fixed output version (5V) of the TPS63070 (adjustable output 2.5 - 9V)
RJ45 connector to the I2C shield
POWER FLAGS
VCCQ & GNDS (ISOLATED SUPPLY)
Note: The original Atlas design (public domain) has a OFF pin. This was not kept in the design since there no 5th pin available in the CAT cable and power is cut by multiplexer when needed.
PROBE GND
Weak
Pull-up resistors to isolated supply
Decoupling capacitor for ISO1540 input
CONNECTION TO ATLAS EZO PH PCB
Pull-up resistors
VOLTAGE REGULATING CIRCUIT (BASED ON BUCK-BOOST CONVERTER WITH SWITCH CURRENT)
VCC
ISOLATED SUPPLY AND ISOLATED I2C
NOTE: +5V is the WEAK SUPPLY (POST-NANO, PRE-REGULATOR) VCC is the CLEAN SUPPLY (POST-RFM-0505S) VCCQ is the ISOLATED SUPPLY GND is the UNISOLATED GROUND FOR GENERAL USAGE GNDS is the ISOLATED GROUND ("S" for SIGNAL) (PRE-EZO-PH)
<<---
ISO1540 DIGITAL SIGNAL ISOLATION CIRCUIT
-> ISOLATED
Decoupling caps for power input
TPS630701 accuracy (PWM mode only): +/- 1%
VOUT: Fixed 5V
+5V
EVISUN B0505S (UNREGULATED DC-DC CONVERTER)
GENERAL
Note: The voltage regulator circuit transforms the 4.5V +/- 0.5V of the Arduino output to a 5V+/- 0.1% to feed the DC-DC converter.
PROBE +
VIN: 2 - 16V
-------------------------------
Note: For availability and cost reduction, the SI8600 ($8US) from the original design (Atlas) has been substituted with ISO1540 ($1US) by Texas Instruments (recommended).

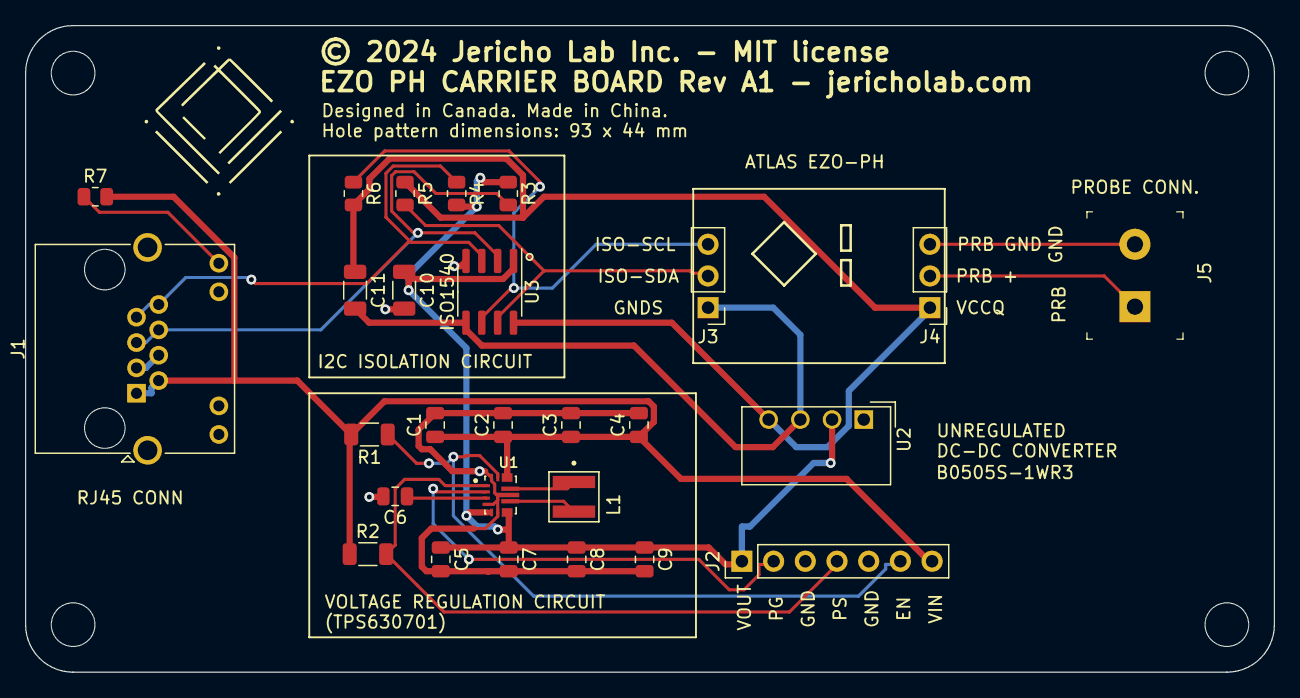
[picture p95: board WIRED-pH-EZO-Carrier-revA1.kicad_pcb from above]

Board: 2 copper layers, 100.1 x 51.8 mm, 33 parts (1 on the bottom side), 18 nets.

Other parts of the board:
G1: LOGO; Do not throw to garbage logo WEEE2
G2: LOGO; jericho-logo-kicad
H1, H2, H3, H4: MountingHole_3.5mm

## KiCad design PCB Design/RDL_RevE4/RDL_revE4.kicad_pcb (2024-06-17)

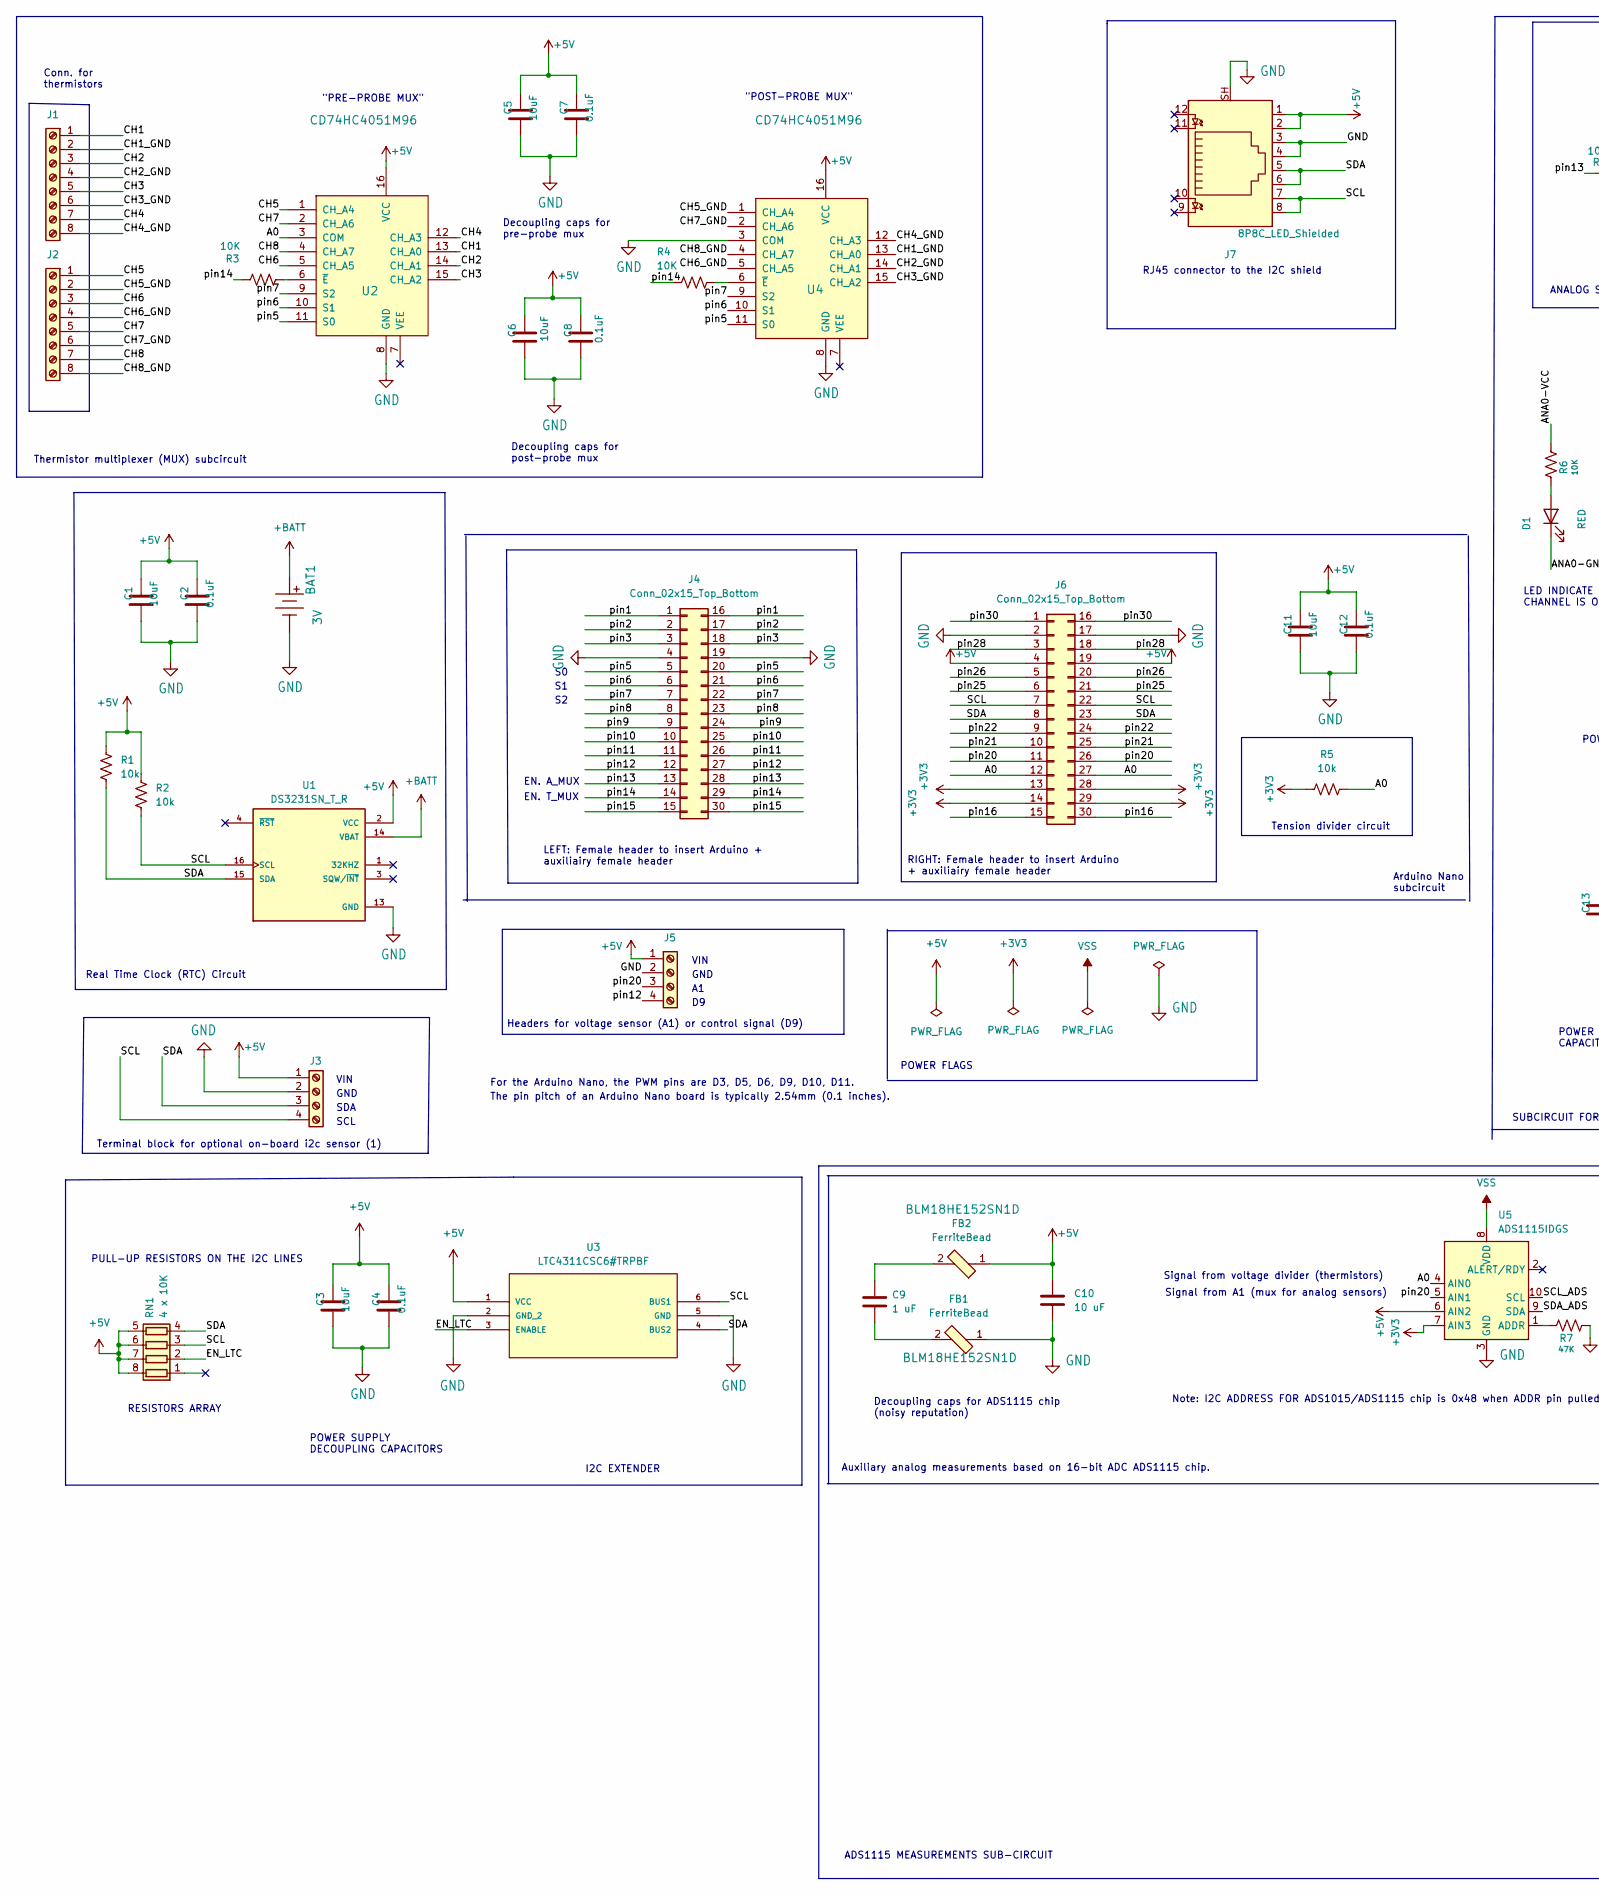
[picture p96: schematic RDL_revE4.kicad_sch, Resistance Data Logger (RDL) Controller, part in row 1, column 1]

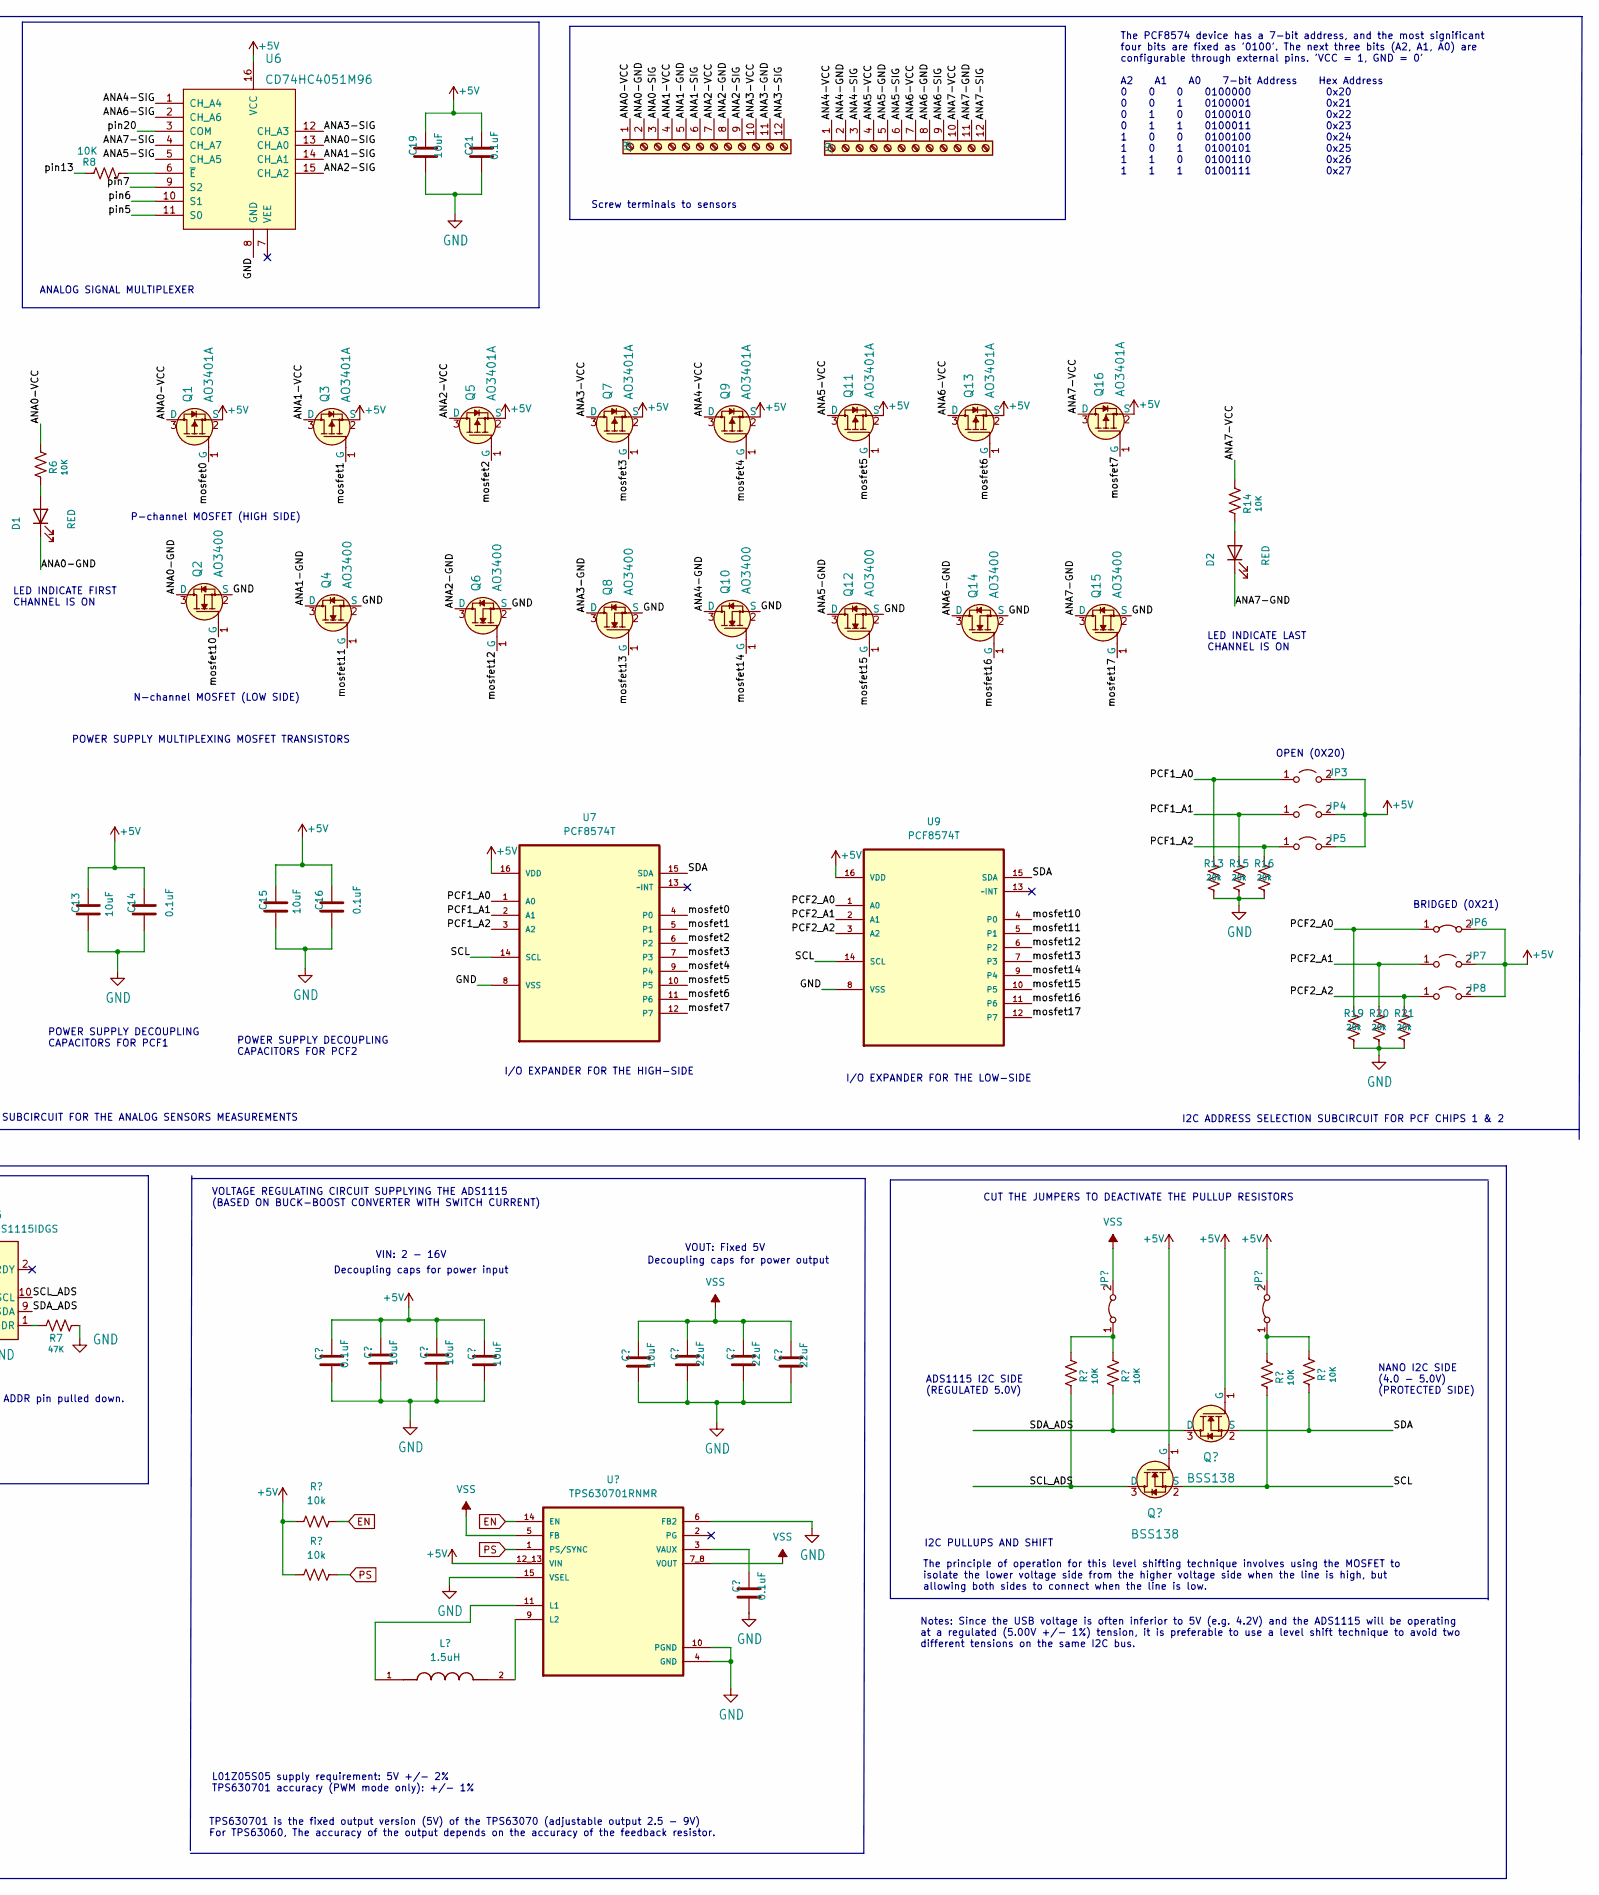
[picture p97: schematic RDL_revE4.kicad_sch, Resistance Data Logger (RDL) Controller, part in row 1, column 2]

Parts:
BAT1: 3V; BatteryHolder_Keystone_3000_1x12mm-Edited; MPN BS-7; Digi-Key_PN BS-7-ND
C1, C3, C5, C6, C11, C13, C15, C18, C19, C20, C22, C23: 10uF; C_0805_2012Metric; LCSC C440198
C2, C4, C7, C8, C12, C14, C16, C17, C21, C26: 0.1uF; C_0805_2012Metric; LCSC C49678
C9: 1 uF; C_1206_3216Metric; LCSC C1848
C10: 10 uF; C_1206_3216Metric; LCSC C13585
C24, C25, C27: 22uF; C_0805_2012Metric; LCSC C45783
D1, D2: RED; D_0603_1608Metric; LCSC C2286
FB1, FB2: FerriteBead; 0603; MPN BLM18HE152SN1D; Digi-Key_PN 490-5216-1-ND
J1: Screw_Terminal_01x08; Term_Block_1x8_P5mm; LCSC C395863
J2: Term_Block_1x8_P5mm; LCSC C395863
J3: Screw_Terminal_01x04; Term_Block_1x4_P5mm; LCSC C424682
J4, J6: Conn_02x15_Top_Bottom; PinHeader_2x15_P2.54mm_Vertical_Jericho; LCSC C7499350
J5: Term_Block_1x4_P5mm; LCSC C424682
J7: 8P8C_LED_Shielded; RJ45_Amphenol_RJHSE538X; LCSC C386757
J8, J9: Screw_Terminal_01x12; TerminalBlock_Phoenix_PT-1,5-12-5.0-H_1x12_P5.00mm_Horizont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; LCSC C5290376
JP1, JP2: Jumper_2_Bridged; SolderJumper-2_P1.3mm_Bridged_Pad1.0x1.5mm-Edited
JP3, JP4, JP5, JP7, JP8: Jumper_2_Bridged; SolderJumper-2_P1.3mm_Open_TrianglePad1.0x1.5mm
JP6: Jumper_2_Bridged; SolderJumper-2_P1.3mm_Bridged_Pad1.0x1.5mm
L1: 1.5uH; IND_XFL4020-152MEC; PARTREV 11/02/18; LCSC C167802
Q1, Q3, Q5, Q7, Q9, Q11, Q13, Q16: AO3401A; SOT-23-3; MPN AO3401A; Digi-Key_PN 785-1001-1-ND
Q2, Q4, Q6, Q8, Q10, Q12, Q14, Q15: AO3400; SOT-23-3; MPN 2N7002; Digi-Key_PN 2N7002NCT-ND
Q17, Q18: BSS138; SOT-23-3; MPN BSS138; Digi-Key_PN BSS138CT-ND
R1, R2, R9, R10: 10k; R_1206_3216Metric; LCSC C17902
R3, R4, R8: 10K; R_1206_3216Metric; LCSC C17902
R5: 10k; R_1206_3216Metric_Pad1.30x1.75mm_HandSolder; LCSC C319946
R6, R11, R12, R14, R17, R18: 10K; R_0805_2012Metric; LCSC C17414
R7: 47K; R_0805_2012Metric; LCSC C17713
R13, R15, R16, R19, R20, R21: 20k; R_0805_2012Metric; LCSC C4328
RN1: 4 x 10K; R_Array_Convex_4x0603; LCSC C29718
U1: DS3231SN_T_R; SOIC127P1032X265-16N; LCSC C9866
U2, U4, U6: CD74HC4051M96; SOP-16_3.9x9.9mm_P1.27mm-Edited; MPN CD74HC4051E; Digi-Key_PN 296-12810-5-ND
U3: LTC4311CSC6#TRPBF; SC70-SC6; MANUFACTURER_PART_NUMBER ltc4311csc6#pbf; LCSC C580856
U5: ADS1115IDGS; TSSOP-10_3x3mm_P0.5mm; LCSC C37593
U7, U9: PCF8574T; SOIC127P1032X265-16N_FRED_MODIFIED; MPN PCF8574T; LCSC C2987288
U8: TPS630701RNMR; VREG_TPS63070RNMR; LCSC C2876599

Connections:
+3V3: J6.13, J6.14, J6.28, J6.29, R5.2, U5.7 (AIN3)
+5V: C1.1, C2.1, C3.1, C4.1, C5.1, C6.1, C7.1, C8.1, C10.1, C11.1, C12.1, C13.1, C14.1, C15.1, C16.1, C17.1, C18.1, C19.1, C20.1, C21.1, C22.1, FB2.1, J3.1, J5.1, J6.4, J6.19, J7.1, J7.2, JP2.2 (B), JP3.2 (B), JP4.2 (B), JP5.2 (B), JP6.2 (B), JP7.2 (B), JP8.2 (B), Q1.2 (S), Q3.2 (S), Q5.2 (S), Q7.2 (S), Q9.2 (S), Q11.2 (S), Q13.2 (S), Q16.2 (S), Q17.1 (G), Q18.1 (G), R1.1, R2.1, R9.2, R10.1, RN1.5 (R4.2), RN1.6 (R3.2), RN1.7 (R2.2), RN1.8 (R1.2), U1.2 (VCC), U2.16 (VCC), U3.1 (VCC), U4.16 (VCC), U5.6 (AIN2), U6.16 (VCC), U7.16 (VDD), U8.12_13 (VIN), U9.16 (VDD)
+BATT: BAT1.Pos, U1.14 (VBAT)
/A0: J6.12, J6.27, R5.1, U2.3 (COM), U5.4 (AIN0)
/ANA0-GND: D1.1 (K), J8.2, Q2.3 (D)
/ANA0-SIG: J8.3, U6.13 (CH_A0)
/ANA0-VCC: J8.1, Q1.3 (D), R6.2
/ANA1-GND: J8.5, Q4.3 (D)
/ANA1-SIG: J8.6, U6.14 (CH_A1)
/ANA1-VCC: J8.4, Q3.3 (D)
/ANA2-GND: J8.8, Q6.3 (D)
/ANA2-SIG: J8.9, U6.15 (CH_A2)
/ANA2-VCC: J8.7, Q5.3 (D)
/ANA3-GND: J8.11, Q8.3 (D)
/ANA3-SIG: J8.12, U6.12 (CH_A3)
/ANA3-VCC: J8.10, Q7.3 (D)
/ANA4-GND: J9.2, Q10.3 (D)
/ANA4-SIG: J9.3, U6.1 (CH_A4)
/ANA4-VCC: J9.1, Q9.3 (D)
/ANA5-GND: J9.5, Q12.3 (D)
/ANA5-SIG: J9.6, U6.5 (CH_A5)
/ANA5-VCC: J9.4, Q11.3 (D)
/ANA6-GND: J9.8, Q14.3 (D)
/ANA6-SIG: J9.9, U6.2 (CH_A6)
/ANA6-VCC: J9.7, Q13.3 (D)
/ANA7-GND: D2.1 (K), J9.11, Q15.3 (D)
/ANA7-SIG: J9.12, U6.4 (CH_A7)
/ANA7-VCC: J9.10, Q16.3 (D), R14.2
/CH1: J1.1, U2.13 (CH_A0)
/CH1_GND: J1.2, U4.13 (CH_A0)
/CH2: J1.3, U2.14 (CH_A1)
/CH2_GND: J1.4, U4.14 (CH_A1)
/CH3: J1.5, U2.15 (CH_A2)
/CH3_GND: J1.6, U4.15 (CH_A2)
/CH4: J1.7, U2.12 (CH_A3)
/CH4_GND: J1.8, U4.12 (CH_A3)
/CH5: J2.1, U2.1 (CH_A4)
/CH5_GND: J2.2, U4.1 (CH_A4)
/CH6: J2.3, U2.5 (CH_A5)
/CH6_GND: J2.4, U4.5 (CH_A5)
/CH7: J2.5, U2.2 (CH_A6)
/CH7_GND: J2.6, U4.2 (CH_A6)
/CH8: J2.7, U2.4 (CH_A7)
/CH8_GND: J2.8, U4.4 (CH_A7)
/EN_LTC: RN1.2 (R2.1), U3.3 (ENABLE)
/PCF1_A0: JP3.1 (A), R13.1, U7.1 (A0)
/PCF1_A1: JP4.1 (A), R15.1, U7.2 (A1)
/PCF1_A2: JP5.1 (A), R16.1, U7.3 (A2)
/PCF2_A0: JP6.1 (A), R19.1, U9.1 (A0)
/PCF2_A1: JP7.1 (A), R20.1, U9.2 (A1)
/PCF2_A2: JP8.1 (A), R21.1, U9.3 (A2)
/SCL: J3.4, J6.7, J6.22, J7.7, J7.8, Q17.2 (S), R2.2, R17.1, RN1.3 (R3.1), U1.16 (SCL), U3.6 (BUS1), U7.14 (SCL), U9.14 (SCL)
/SCL_ADS: Q17.3 (D), R11.1, U5.10 (SCL)
/SDA: J3.3, J6.8, J6.23, J7.5, J7.6, Q18.2 (S), R1.2, R18.1, RN1.4 (R4.1), U1.15 (SDA), U3.4 (BUS2), U7.15 (SDA), U9.15 (SDA)
/SDA_ADS: Q18.3 (D), R12.1, U5.9 (SDA)
/mosfet0: Q1.1 (G), U7.4 (P0)
/mosfet1: Q3.1 (G), U7.5 (P1)
/mosfet2: Q5.1 (G), U7.6 (P2)
/mosfet3: Q7.1 (G), U7.7 (P3)
/mosfet4: Q9.1 (G), U7.9 (P4)
/mosfet5: Q11.1 (G), U7.10 (P5)
/mosfet6: Q13.1 (G), U7.11 (P6)
/mosfet7: Q16.1 (G), U7.12 (P7)
/mosfet10: Q2.1 (G), U9.4 (P0)
/mosfet11: Q4.1 (G), U9.5 (P1)
/mosfet12: Q6.1 (G), U9.6 (P2)
/mosfet13: Q8.1 (G), U9.7 (P3)
/mosfet14: Q10.1 (G), U9.9 (P4)
/mosfet15: Q12.1 (G), U9.10 (P5)
/mosfet16: Q14.1 (G), U9.11 (P6)
/mosfet17: Q15.1 (G), U9.12 (P7)
/pin1: J4.1, J4.16
/pin2: J4.2, J4.17
/pin3: J4.3, J4.18
/pin5: J4.5, J4.20, U2.11 (S0), U4.11 (S0), U6.11 (S0)
/pin6: J4.6, J4.21, U2.10 (S1), U4.10 (S1), U6.10 (S1)
/pin7: J4.7, J4.22, U2.9 (S2), U4.9 (S2), U6.9 (S2)
/pin8: J4.8, J4.23
/pin9: J4.9, J4.24
/pin10: J4.10, J4.25
/pin11: J4.11, J4.26
/pin12: J4.12, J4.27, J5.4
/pin13: J4.13, J4.28, R8.1
/pin14: J4.14, J4.29, R3.2, R4.2
/pin15: J4.15, J4.30
/pin16: J6.15, J6.30
/pin20: J5.3, J6.11, J6.26, U5.5 (AIN1), U6.3 (COM)
/pin21: J6.10, J6.25
/pin22: J6.9, J6.24
/pin25: J6.6, J6.21
/pin26: J6.5, J6.20
/pin28: J6.3, J6.18
/pin30: J6.1, J6.16
EN: R9.1, U8.14 (EN)
GND: BAT1.Neg, C1.2, C2.2, C3.2, C4.2, C5.2, C6.2, C7.2, C8.2, C10.2, C11.2, C12.2, C13.2, C14.2, C15.2, C16.2, C17.2, C18.2, C19.2, C20.2, C21.2, C22.2, C23.2, C24.2, C25.2, C26.2, C27.2, FB1.1, J3.2, J4.4, J4.19, J5.2, J6.2, J6.17, J7.3, J7.4, J7.SH, Q2.2 (S), Q4.2 (S), Q6.2 (S), Q8.2 (S), Q10.2 (S), Q12.2 (S), Q14.2 (S), Q15.2 (S), R7.2, R13.2, R15.2, R16.2, R19.2, R20.2, R21.2, U1.13 (GND), U2.8 (GND), U3.2 (GND_2), U3.5 (GND), U4.3 (COM), U4.8 (GND), U5.3 (GND), U6.8 (GND), U7.8 (VSS), U8.4 (GND), U8.6 (FB2), U8.10 (PGND), U8.15 (VSEL), U9.8 (VSS)
unnamed: C9.1, FB2.2
unnamed: C9.2, FB1.2
unnamed: D1.2 (A), R6.1
unnamed: D2.2 (A), R14.1
unnamed: JP1.1 (A), R11.2, R12.2
unnamed: JP2.1 (A), R17.2, R18.2
unnamed: R3.1, U2.6 (~E)
unnamed: R4.1, U4.6 (~E)
unnamed: R7.1, U5.1 (ADDR)
unnamed: R8.2, U6.6 (~E)
unnamed: L1.1, U8.11 (L1)
unnamed: L1.2, U8.9 (L2)
unnamed: C26.1, U8.3 (VAUX)
PS: R10.2, U8.1 (PS/SYNC)
VSS: C23.1, C24.1, C25.1, C27.1, JP1.2 (B), U5.8 (VDD), U8.5 (FB), U8.7_8 (VOUT)

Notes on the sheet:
EN. T_MUX
Thermistor multiplexer (MUX) subcircuit
N-channel MOSFET (LOW SIDE)
Arduino Nano subcircuit
I/O EXPANDER FOR THE HIGH-SIDE
The principle of operation for this level shifting technique involves using the MOSFET to isolate the lower voltage side from the higher voltage side when the line is high, but allowing both sides to connect when the line is low.
Notes: Since the USB voltage is often inferior to 5V (e.g. 4.2V) and the ADS1115 will be operating at a regulated (5.00V +/- 1%) tension, it is preferable to use a level shift technique to avoid two different tensions on the same I2C bus.
L01Z05S05 supply requirement: 5V +/- 2% TPS630701 accuracy (PWM mode only): +/- 1%
LEFT: Female header to insert Arduino + auxiliairy female header
P-channel MOSFET (HIGH SIDE)
POWER SUPPLY DECOUPLING CAPACITORS
Decoupling caps for ADS1115 chip (noisy reputation)
SCL
LED INDICATE FIRST CHANNEL IS ON
Terminal block for optional on-board i2c sensor (1)
Real Time Clock (RTC) Circuit
Note: I2C ADDRESS FOR ADS1015/ADS1115 chip is 0x48 when ADDR pin pulled down.
TPS630701 is the fixed output version (5V) of the TPS63070 (adjustable output 2.5 - 9V) For TPS63060, The accuracy of the output depends on the accuracy of the feedback resistor.
GND
VIN: 2 - 16V
Decoupling caps for power output
Auxiliary analog measurements based on 16-bit ADC ADS1115 chip.
POWER SUPPLY MULTIPLEXING MOSFET TRANSISTORS
BRIDGED (0X21)
LED INDICATE LAST CHANNEL IS ON
Decoupling caps for post-probe mux
Signal from A1 (mux for analog sensors)
VIN
"POST-PROBE MUX"
I2C PULLUPS AND SHIFT
SDA
PULL-UP RESISTORS ON THE I2C LINES
"PRE-PROBE MUX"
ADS1115 MEASUREMENTS SUB-CIRCUIT
Conn. for thermistors
Decoupling caps for power input
I2C ADDRESS SELECTION SUBCIRCUIT FOR PCF CHIPS 1 & 2
VOLTAGE REGULATING CIRCUIT SUPPLYING THE ADS1115 (BASED ON BUCK-BOOST CONVERTER WITH SWITCH CURRENT)
The pin pitch of an Arduino Nano board is typically 2.54mm (0.1 inches).
RESISTORS ARRAY

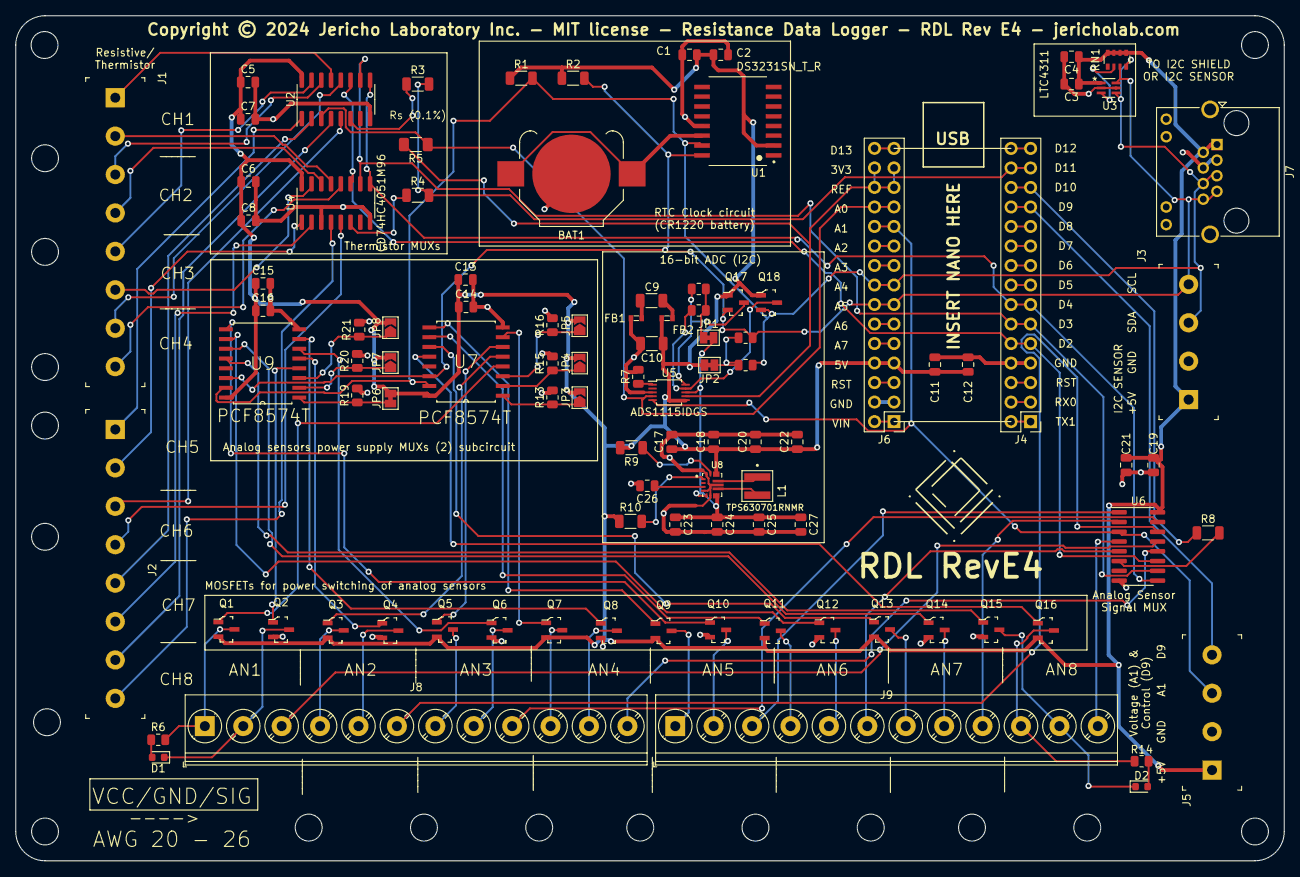
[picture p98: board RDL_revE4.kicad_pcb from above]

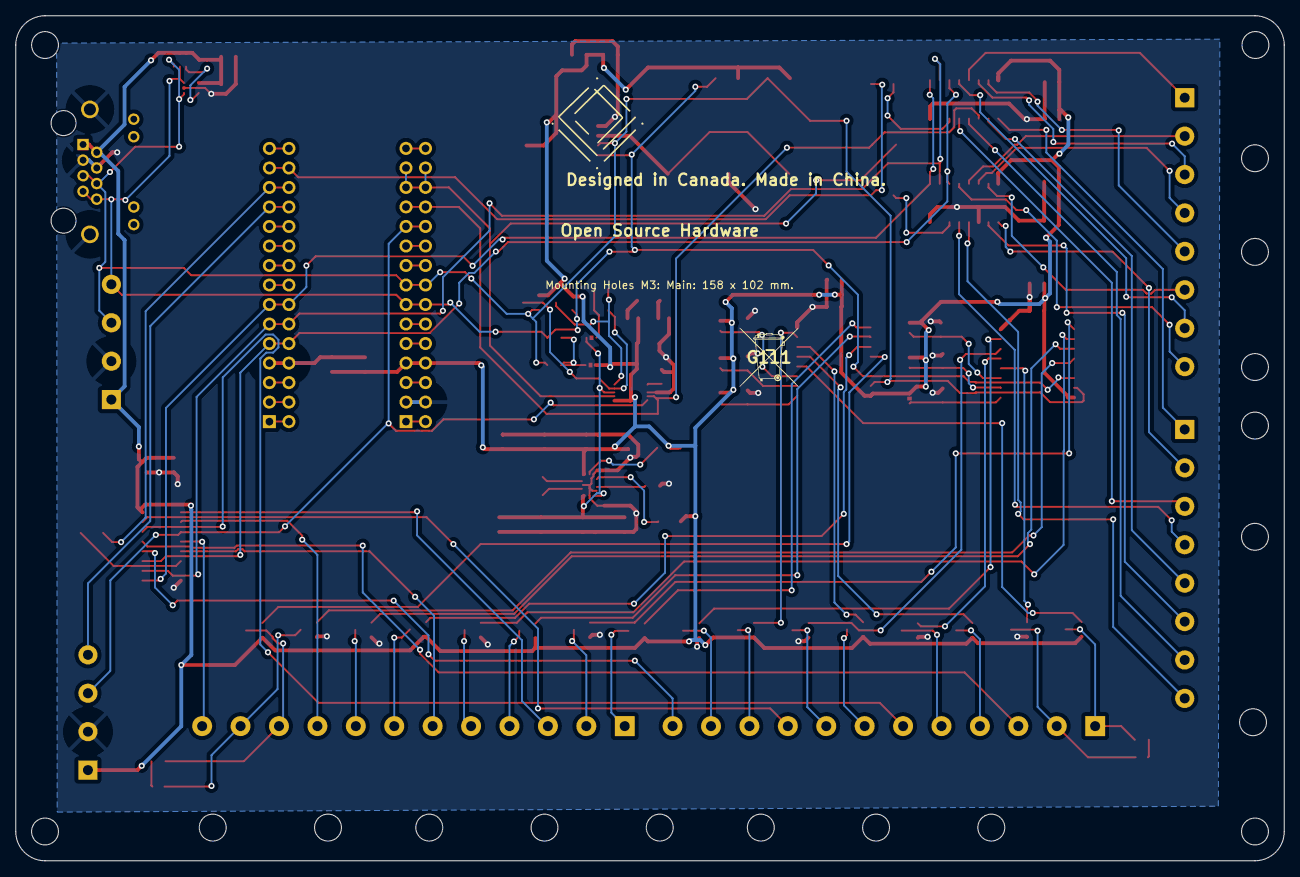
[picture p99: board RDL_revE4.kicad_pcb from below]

Board: 2 copper layers, 165.1 x 110.0 mm, 120 parts (2 on the bottom side), 110 nets.

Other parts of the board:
G111: LOGO; Do not throw to garbage logo WEEE2
G222, G222#2: LOGO; jericho-logo-kicad
H6, H7, H51: MountingHole_3.5mm
REF3, REF4, REF5, REF6, REF7, REF8, REF9, REF10, REF11, REF13, REF14, REF15, REF16, REF17, REF18: MountingHole_3.5mm

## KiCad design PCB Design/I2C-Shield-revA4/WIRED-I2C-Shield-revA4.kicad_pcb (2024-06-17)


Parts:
C1, C2, C5: 10uF; C_0805_2012Metric; LCSC C15850
C3, C4, C6: 0.1uF; C_0805_2012Metric; LCSC C49678
D1, D2: RED; D_0603_1608Metric; LCSC C2286
J1, J2, J3, J4, J5, J6, J7, J9, J10: RJ45; RJ45_Amphenol_54602-x08_Horizontal; LCSC C3000197
J8: 8P8C_LED; RJ45_Amphenol_RJHSE538X; LCSC C386757
JP1, JP2, JP3, JP6, JP8, JP11: Jumper_2_Bridged; SolderJumper-2_P1.3mm_Open_Pad1.0x1.5mm
JP4, JP5: Jumper_2_Bridged; SolderJumper-2_P1.3mm_Bridged_Pad1.0x1.5mm
JP7, JP9, JP10: Jumper_2_Bridged; SolderJumper-2_P1.3mm_Bridged_Pad1.0x1.5mm-Edited
Q1, Q4, Q6, Q8, Q10, Q12, Q14, Q15: AO3406; SOT-23-3; MPN 2N7002; Digi-Key_PN 2N7002NCT-ND
Q2, Q3, Q5, Q7, Q9, Q11, Q13, Q16: AO3401A; SOT-23-3; MPN AO3401A; Digi-Key_PN 785-1001-1-ND
R1, R2, R3, R9, R10, R11, R12, R13, R14: 20k; R_0805_2012Metric; LCSC C4328
R4, R5, R6, R7, R15: 10K; R_0805_2012Metric; LCSC C17414
R8: 100K; R_0805_2012Metric; LCSC C149504
U1, U3: PCF8574T; SOIC127P1032X265-16N; MPN PCF8574T; LCSC C2987288
U2: TCA9548APWR; TSSOP-24_W4.40mm; MPN TCA9548APWR; Digi-Key_PN 296-34905-1-ND

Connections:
/0GND: D2.1 (K), J1.3, J1.4, Q1.3 (D)
/0SCL: J1.7, J1.8, U2.5 (SC0)
/0SDA: J1.5, J1.6, U2.4 (SD0)
/0VCC: J1.1, J1.2, Q2.3 (D), R7.2
/1GND: J2.3, J2.4, Q4.3 (D)
/1SCL: J2.7, J2.8, U2.7 (SC1)
/1SDA: J2.5, J2.6, U2.6 (SD1)
/1VCC: J2.1, J2.2, Q3.3 (D)
/2GND: J3.3, J3.4, Q6.3 (D)
/2SCL: J3.7, J3.8, U2.9 (SC2)
/2SDA: J3.5, J3.6, U2.8 (SD2)
/2VCC: J3.1, J3.2, Q5.3 (D)
/3GND: J4.3, J4.4, Q8.3 (D)
/3SCL: J4.7, J4.8, U2.11 (SC3)
/3SDA: J4.5, J4.6, U2.10 (SD3)
/3VCC: J4.1, J4.2, Q7.3 (D)
/4GND: J5.3, J5.4, Q10.3 (D)
/4SCL: J5.7, J5.8, U2.14 (SC4)
/4SDA: J5.5, J5.6, U2.13 (SD4)
/4VCC: J5.1, J5.2, Q9.3 (D)
/5GND: J6.3, J6.4, Q12.3 (D)
/5SCL: J6.7, J6.8, U2.16 (SC5)
/5SDA: J6.5, J6.6, U2.15 (SD5)
/5VCC: J6.1, J6.2, Q11.3 (D)
/6GND: J7.3, J7.4, Q14.3 (D)
/6SCL: J7.7, J7.8, U2.18 (SC6)
/6SDA: J7.5, J7.6, U2.17 (SD6)
/6VCC: J7.1, J7.2, Q13.3 (D)
/7GND: J8.3, J8.4, J8.11, J8.SH, Q15.3 (D)
/7SCL: J8.7, J8.8, U2.20 (SC7)
/7SDA: J8.5, J8.6, U2.19 (SD7)
/7VCC: J8.1, J8.2, Q16.3 (D), R15.2
/INPUTSCL: J9.7, J9.8, J10.7, J10.8, JP4.1 (A), U1.14 (SCL), U2.22 (SCL), U3.14 (SCL)
/INPUTSDA: J9.5, J9.6, J10.5, J10.6, JP5.1 (A), U1.15 (SDA), U2.23 (SDA), U3.15 (SDA)
/PCF1_A0: JP6.1 (A), R9.1, U1.1 (A0)
/PCF1_A1: JP7.1 (A), R10.1, U1.2 (A1)
/PCF1_A2: JP8.1 (A), R11.1, U1.3 (A2)
/PCF2_A0: JP9.1 (A), R12.1, U3.1 (A0)
/PCF2_A1: JP10.1 (A), R13.1, U3.2 (A1)
/PCF2_A2: JP11.1 (A), R14.1, U3.3 (A2)
/RESET: R8.1, U2.3 (~RES)
/TCA_A0: JP1.1 (A), R1.1, U2.1 (A0)
/TCA_A1: JP2.1 (A), R2.1, U2.2 (A1)
/TCA_A2: JP3.1 (A), R3.1, U2.21 (A2)
/mosfet0: Q2.1 (G), U1.4 (P0)
/mosfet1: Q3.1 (G), U1.5 (P1)
/mosfet2: Q5.1 (G), U1.6 (P2)
/mosfet3: Q7.1 (G), U1.7 (P3)
/mosfet4: Q9.1 (G), U1.9 (P4)
/mosfet5: Q11.1 (G), U1.10 (P5)
/mosfet6: Q13.1 (G), U1.11 (P6)
/mosfet7: Q16.1 (G), U1.12 (P7)
/mosfet10: Q1.1 (G), U3.4 (P0)
/mosfet11: Q4.1 (G), U3.5 (P1)
/mosfet12: Q6.1 (G), U3.6 (P2)
/mosfet13: Q8.1 (G), U3.7 (P3)
/mosfet14: Q10.1 (G), U3.9 (P4)
/mosfet15: Q12.1 (G), U3.10 (P5)
/mosfet16: Q14.1 (G), U3.11 (P6)
/mosfet17: Q15.1 (G), U3.12 (P7)
GND: C1.2, C2.2, C3.2, C4.2, C5.2, C6.2, D1.1 (K), J9.3, J9.4, J10.3, J10.4, Q1.2 (S), Q4.2 (S), Q6.2 (S), Q8.2 (S), Q10.2 (S), Q12.2 (S), Q14.2 (S), Q15.2 (S), R1.2, R2.2, R3.2, R9.2, R10.2, R11.2, R12.2, R13.2, R14.2, U1.8 (VSS), U2.12 (GND), U3.8 (VSS)
unnamed: D1.2 (A), R4.1
unnamed: D2.2 (A), R7.1
unnamed: J8.12, R15.1
unnamed: JP4.2 (B), R5.1
unnamed: JP5.2 (B), R6.1
VCC: C1.1, C2.1, C3.1, C4.1, C5.1, C6.1, J9.1, J9.2, J10.1, J10.2, JP1.2 (B), JP2.2 (B), JP3.2 (B), JP6.2 (B), JP7.2 (B), JP8.2 (B), JP9.2 (B), JP10.2 (B), JP11.2 (B), Q2.2 (S), Q3.2 (S), Q5.2 (S), Q7.2 (S), Q9.2 (S), Q11.2 (S), Q13.2 (S), Q16.2 (S), R4.2, R5.2, R6.2, R8.2, U1.16 (VDD), U2.24 (VCC), U3.16 (VDD)

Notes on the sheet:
LED INDICATES MOSFET CHANNEL 8 IS POWERED ON
I/O EXPANDER FOR THE HIGH?-SIDE
Cutting the solder jumpers will deactivate the pull-up resistors
RJ45 CONNECTOR FROM RDL TO I2C SHIELD + RJ45 FOR DAISY CHAIN TO POTENTIAL 2ND I2C SHIELD
LED LIGHT TO INDICATE MAIN POWER ON
I2C ADDRESS SELECTION SUBCIRCUIT FOR TCA CHIP
I2C MULTIPLEXER FOR THE SDA AND SCL LINES OF THE SENSORS
POWER SUPPLY DECOUPLING CAPACITORS
I2C ADDRESS SELECTION SUBCIRCUIT FOR PCF CHIPS 2 (ADDRESS 0x23)
SUBCIRCUIT: I2C MULTIPLEXERS FOR THE POWER SUPPLY OF THE SENSORS (NOISE REDUCTION)
Weak pull-up resistor on Reset pin to avoid unwanted reset of the chip. Ground signal would reset the chip.
POWER SUPPLY DECOUPLING CAPACITORS FOR PCF2
POWER SUPPLY DECOUPLING CAPACITORS FOR PCF1
TCA has a feature that PCA does not have (operate i2c device with voltage different than the 5V i2c bus) See specs.
POWER SUPPLY MULTIPLEXING TRANSISTORS SUBCIRCUIT
I/O EXPANDER FOR THE LOW-SIDE
RJ45 pins order (VCC, GND,SDA,SCL) of the present shield and the connected devices should match.
P-channel MOSFET (HIGH SIDE)
TEST: CH 8 HAS LEDS.
LED INDICATES MOSFET CHANNEL 0 IS POWERED ON
RJ45 CONNECTORS FOR I2C DEVICES
N-channel MOSFET (LOW SIDE)
I2C ADDRESS SELECTION SUBCIRCUIT FOR PCF CHIPS 1 (ADDRESS 0x22)
Pull down A0,A1,A2 gives 0x70 address to TCA device
The PCF8574 device has a 7-bit address, and the most significant four bits are fixed as '0100'. The next three bits (A2, A1, A0) are configurable through external pins. 'VCC = 1, GND = 0' A2 A1 A0 7-bit Address Hex Address 0 0 0 0100000 0x20 0 0 1 0100001 0x21 0 1 0 0100010 0x22 0 1 1 0100011 0x23 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



Board: 2 copper layers, 165.1 x 110.0 mm, 70 parts (2 on the bottom side), 67 nets.

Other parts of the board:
G1, G2: LOGO; jericho-logo-kicad
G3: LOGO; Do not throw to garbage logo WEEE2
H1, H2, H3, H4: MountingHole_3.5mm

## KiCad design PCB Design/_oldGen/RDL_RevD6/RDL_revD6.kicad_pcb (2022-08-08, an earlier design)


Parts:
A1: Arduino_Nano_v3.x; Arduino_Nano
BAT1: 3V; BatteryHolder_Keystone_3000_1x12mm; MPN BS-7; Digi-Key_PN BS-7-ND
C1: 1 uF; C_1206_3216Metric
J1, J2, J3, J5: Screw_Terminal_01x08; Term_Block_1x8_P5mm
J4, J6: Term_Block_1x8_P5mm
J7, J8, J10, J11: Screw_Terminal_01x15; PinHeader_1x08_P2.54mm_Vertical
J9, J13: Term_Block_1x4_P5mm
J12: Screw_Terminal_01x04; Term_Block_1x4_P5mm
J14: Term_Block_1x2_P5mm; MPN OSTTC020162; Digi-Key_PN ED2600-ND
J15: OSTTC020162; Term_Block_1x2_P5mm; MPN OSTTC020162; Digi-Key_PN ED2600-ND
R1, R2: 10k; R_1206_3216Metric
R3: 10K; R_1206_3216Metric; LCSC C269752
R4: 10K; R_Axial_DIN0207_L6.3mm_D2.5mm_P15.24mm_Horizontal
U1: DS1307ZN+; SOIC-8_3.9x4.9mm_P1.27mm
U2: CD74HC4067M96; SOIC-24_W7.50mm; MPN CD74HC4067M96; Digi-Key_PN 296-29408-1-ND
Y1: Crystal; Crystal_SMD_Abracon_ABS25-4Pin_8.0x3.8mm

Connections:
+BATT: BAT1.1, BAT1.Pos, U1.3 (VBAT)
/CH1: J1.1, J3.1, U2.9 (I0)
/CH2: J1.3, J3.3, U2.8 (I1)
/CH3: J1.5, J3.5, U2.7 (I2)
/CH4: J1.7, J3.7, U2.6 (I3)
/CH5: J2.1, J4.1, U2.5 (I4)
/CH6: J2.3, J4.3, U2.4 (I5)
/CH7: J2.5, J4.5, U2.3 (I6)
/CH8: J2.7, J4.7, U2.2 (I7)
/CH9: J5.1, U2.23 (I8)
/CH10: J5.3, U2.22 (I9)
/CH11: J5.5, U2.21 (I10)
/CH12: J5.7, U2.20 (I11)
/CH13: J6.1, U2.19 (I12)
/CH14: J6.3, U2.18 (I13)
/CH15: J6.5, U2.17 (I14)
/CH16: J6.7, U2.16 (I15)
/GND: A1.4 (GND), BAT1.2, BAT1.Neg, C1.2, J1.2, J1.4, J1.6, J1.8, J2.2, J2.4, J2.6, J2.8, J3.2, J3.4, J3.6, J3.8, J4.2, J4.4, J4.6, J4.8, J5.2, J5.4, J5.6, J5.8, J6.2, J6.4, J6.6, J6.8, J7.4, J9.2, J12.2, J13.2, J14.2, J15.1, U1.4 (GND), U2.12 (GND)
/OSCI: U1.1 (X1), Y1.1
/OSCO: U1.2 (X2), Y1.2
/SCL: A1.24 (A5), J10.7, J12.4, J13.4, R2.2, U1.6 (SCL)
/SDA: A1.23 (A4), J10.8, J12.3, J13.3, R1.2, U1.5 (SDA)
/SQW: U1.7 (SQW/OUT)
/VCC15: A1.15 (D12), C1.1, J8.7, J9.1, J12.1, J13.1, R1.1, R2.1, U1.8 (VCC)
/pin1: A1.1 (D1/TX), J7.1
/pin2: A1.2 (D0/RX), J7.2
/pin3: A1.3 (~RESET), J7.3
/pin5: A1.5 (D2), J7.5, U2.10 (S0)
/pin6: A1.6 (D3), J7.6, U2.11 (S1)
/pin7: A1.7 (D4), J7.7, U2.14 (S2)
/pin8: A1.8 (D5), J7.8, U2.13 (S3)
/pin9: A1.9 (D6), J8.1
/pin10: A1.10 (D7), J8.2
/pin11: A1.11 (D8), J8.3
/pin12: A1.12 (D9), J8.4, J9.4
/pin13: A1.13 (D10), J8.5
/pin14: A1.14 (D11), J8.6, R3.2
/pin16: A1.16 (D13), J11.7
/pin17: A1.17 (3V3), A1.18 (AREF), J11.5, J11.6, R4.1
/pin19: A1.19 (A0), J11.4, J14.1, J15.2, R4.2, U2.1 (COM)
/pin20: A1.20 (A1), J9.3, J11.3
/pin21: A1.21 (A2), J11.2
/pin22: A1.22 (A3), J11.1
/pin25: A1.25 (A6), J10.6
/pin26: A1.26 (A7), J10.5
/pin27: A1.27 (+5V), J10.4, U2.24 (VCC)
/pin28: A1.28 (~RESET), J10.3
/pin29: A1.29 (GND), J10.2
/pin30: A1.30 (VIN), J10.1
unnamed: R3.1, U2.15 (E)

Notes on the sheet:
ENABLE MUX
Multiplexer subcircuit
VIN
OSCI Oscillator Input. OSCO Oscillator Output. Crystal has no polarity.
VCC on demand
GND
SCL
SDA
(VCC)
Terminal blocks for optional i2c sensors (e.g. AM2301b humidity sensor)
Real Time Clock (RTC) Circuit based on ADAFRUIT DS1307 breakout board (open source)
Auxiliairy female header for left side of Arduino Nano
Conn. for parallel opt. ceramic caps 221 pF (noise filtering)
Conn. for parallel opt. electrolytic caps (1x 100 uF, 1x 0.1 uF) (noise filtering)
Conn. for thermistors
Auxiliairy female header for right side of Arduino Nano
Terminal blocks for voltage sensor (A1) or control signal (D9)
For the Arduino Nano, the PWM pins are D3, D5, D6, D9, D10, D11.
The MUX has an enable (E) control which when receiving HIGH signal will disable all switches to their "off" state.


Board: 2 copper layers, 162.6 x 94.0 mm, 35 parts (0 on the bottom side), 49 nets.

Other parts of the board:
G1: LOGO; Do not throw to garbage logo WEEE2
G2: LOGO; made-in-canada
H1, H2, H3, H4: MountingHole_2.5mm
H5, H6, H7, H8: MountingHole_3.5mm

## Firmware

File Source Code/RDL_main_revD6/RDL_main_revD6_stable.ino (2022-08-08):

/* RESISTANCE DATA LOGGER (RDL) SOURCE CODE
 * Copyright (c) 2022 Jericho Laboratory Inc.
 * 
 *THIS SOFTWARE IS PROVIDED BY THE COPYRIGHT HOLDERS AND CONTRIBUTORS "AS IS" AND ANY EXPRESS OR IMPLIED WARRANTIES, INCLUDING, BUT NOT LIMITED TO, THE
  IMPLIED WARRANTIES OF MERCHANTABILITY AND FITNESS FOR A PARTICULAR PURPOSE ARE DISCLAIMED. IN NO EVENT SHALL THE COPYRIGHT OWNER OR CONTRIBUTORS BE
  LIABLE FOR ANY DIRECT, INDIRECT, INCIDENTAL, SPECIAL, EXEMPLARY, OR CONSEQUENTIAL DAMAGES (INCLUDING, BUT NOT LIMITED TO, PROCUREMENT OF
  SUBSTITUTE GOODS OR SERVICES; LOSS OF USE, DATA, OR PROFITS; OR BUSINESS INTERRUPTION) HOWEVER CAUSED AND ON ANY THEORY OF LIABILITY, WHETHER IN
  CONTRACT, STRICT LIABILITY, OR TORT (INCLUDING NEGLIGENCE OR OTHERWISE) ARISING IN ANY WAY OUT OF THE USE OF THIS SOFTWARE, EVEN IF ADVISED OF THE
  POSSIBILITY OF SUCH DAMAGE. */

#define __FILENAME_WIN__ (strrchr(__FILE__, '/') ? strrchr(__FILE__, '/') + 1 : __FILE__)   //Creates a C macro based on standard macro __FILE__ that prints the filename instead of system path
#define __FILENAME_LINUX__ (strrchr(__FILE__, '\\') ? strrchr(__FILE__, '\\') + 1 : __FILE__)   // Equivalent macro for linux systems
#define word1 strlen(__FILENAME_WIN__)
#define word2 strlen(__FILENAME_LINUX__)
#define __FILENAME__ ((word1)<(word2)? (__FILENAME_WIN__) : (__FILENAME_LINUX__))  // Linux and Windows do not use the same character. so the preprocessor compares the two lengths and pick the string that worked.

////////// USER PARAMETERS //////////// 

int generic=1;                         // use of generic thermistor coefficients (generic = 1) or custom coefficients for calibrated thermistors (generic = 0)
int headerDisplay=1;                   // optional display of headerprint (1 = yes, 0 = no)
int timeDisplay=1;                     // optional display of timestamp (1 = yes, 0 = no)
int idDisplay=1;                       // optional display of identification number of measurement (1 = yes, 0 = no)
int tDisplay=1;                        // optional display of temperature/illuminance values (1 = yes, 0 = no)
int ohmDisplay = 1;                    // optional display of probes resistance values (ohm) (1 = yes, 0 = no)
int humDisplay = 1;                    // optional calculations and display of relative humidities (1 = yes, 0 = no)
int i2cDisplay = 1;                    // optional display of i2c sensor values (1 = yes, 0 = no)
int WBGTDisplay = 1;                   // optional display of WBGT values (1 = yes, 0 = no)
int SoilDisplay = 1;                   // optional display of soil water content values (1 = yes, 0 = no)
int VoltDisplay = 1;                   // optional display of voltage reading values (1 = yes, 0 = no)
int noiseControl = 0;                  // optional delay when noise filter desired (1 = yes, 0 = no)

////////// PROGRAMMER PARAMETERS ////////////

char sensors[17]="TTTTTTTTTTTTTTTT";            // define array of 16 characters to indicate the type of sensor in each channel  (T=thermistor, P=photoresistor) . Factory default.
char sensors_temp[17]="TTTTTTTTTTTTTTTT";       // initiating the temporary holder
char humidities[9]="ABCD1234";         // define array of 8 elements to indicate the type of sensor in each channel  (letters=dry bulb, numbers = wet bulb). ///////// To be updated.
char humidities_temp[9]="00000000";    // initiating the temporary holder
int WBGT_dry = 1;                      // defining which channel has the dry bulb of the WBGT index  (1 = C1, 2 = C2, etc.)
int WBGT_wet = 4;                      // defining which channel has the wet bulb of the WBGT index  (1 = C1, 2 = C2, etc.)
int WBGT_globe = 3;                    // defining which channel has the globe probe of the WBGT index (1 = C1, 2 = C2, etc.)
int sortedHum[]={-1,-1,-1,-1,-1,-1,-1,-1};   // initiating the array of integers that will hold the sorted humidity channels (later the array (global variable) is modified by sortHum())
unsigned long time1 = 0;               // initialize variable to control read cycles
int numberC=16;                        // default number of active channels. Must be an integer between 1 and 8.
int sensors_present=0;                 // we initialize this variable with 0. If there is valid data on the EEPROM, the boolean will change to 1, and we will use this data for 'sensors'.
int humidities_present=0;              // we initialize this variable with 0. If there is valid data on the EEPROM, the boolean will change to 1, and we will use this data for 'humidities'.
int numberC10 = numberC;               // (ms) Temporary storage variable for quantity of channels used
int units = 0;                         // default temperature units are Celcius (0).
long readInterval = 1000;              // (ms) Default interval at which temperature is measured, then stored in volatile memory SRAM and sent to PC [1000 ms = 1s, 86400000 ms = 1 day]
long readInterval0 = 2000;             // (ms) Temporary storage variable for read interval
int Seriesresistor = 10000;            // (ohms) the value of the series resistor for T1 (based on the specifications of your RDL unit)
#define Bsize round(WriteInterval/ReadInterval) // size of buffer array required to average temperatures
long baudRate = 57600;                // (bps) data rate at which data is transmitted between the Arduino and the PC, through the serial monitor (max = 115200)
#include <EEPROM.h>                    // library required to read and write on the EEPROM memory (library size = 8.3 kB)
#include "RTClib.h"                    // library required for the Real-Time Clock (RTC)
#include <Adafruit_AHTX0.h>            // include the required library
Adafruit_AHTX0 aht;                    // define the aht variable
RTC_DS1307 rtc;                        // define the RTC model number used by the RTClib.h
int R_MUX = 70;                        // Internal resistance of the multiplexer (ohms)
#define NUMSAMPLES 1                   // how many samples to take and average at each reading (smooth the noise)
float V_ref = 5;                       // calibration value for voltage measurements with channel A1 (exact value of the VCC supply must be measured with multimeter for improved accuracy)
int AHT_present = 0;                   //initialize the variable that will indicate if a sensor is present
int score;                             // define the variable "score" for evaluation of user input algorithm
//-------------------------------------------------------------------

char C1_ID[] = "T01";   //Unique serial number of each thermistor used
char C2_ID[] = "T02";
char C3_ID[] = "T03";
char C4_ID[] = "T04"; 
char C5_ID[] = "T05";
char C6_ID[] = "T06";
char C7_ID[] = "T07";
char C8_ID[] = "T08";
char C9_ID[] = "T09";
char C10_ID[] = "T10";
char C11_ID[] = "T11";
char C12_ID[] = "T12";
char C13_ID[] = "T13";
char C14_ID[] = "T14";
char C15_ID[] = "T15";
char C16_ID[] = "T16";

//-------------------------------------------------------------------

// STEINHART-HART GENERIC COEFFICIENTS FOR 10K (B25/50 = 3950K) NTC THERMISTORS

float GEN_A =  1.0222793532E-03;
float GEN_B =  2.5316558834E-04;
float GEN_C =  -5.3213022916E-12;

// COEFFICIENTS MATRIX (COPY/PASTE FROM THE OCTAVE SCRIPT OUTPUT TEXT FILE) (8 decimals minimum required)
// Example: First line and first column is the coefficient A of the Steinhart-Hart model for channel 1. 8 decimals required.

float C[16][3] = {
{1.2610084065E-03, 2.1114631980E-04, 1.9023374978E-07},  
{1.2675806791E-03, 2.0979557309E-04, 1.9822805307E-07},
{1.2638846806E-03, 2.1055130024E-04, 1.9382524717E-07},
{1.2718419861E-03, 2.0908957579E-04, 1.9934840352E-07},
{1.2670354615E-03, 2.0990013899E-04, 1.9774405298E-07},
{1.2461782151E-03, 2.1381439152E-04, 1.8265011582E-07},
{1.2534484825E-03, 2.1247717154E-04, 1.8637129521E-07},
{1.2592342994E-03, 2.1205448461E-04, 1.8599202135E-07},
{1.2592342994E-03, 2.1205448461E-04, 1.8599202135E-07},
{1.2592342994E-03, 2.1205448461E-04, 1.8599202135E-07},
{1.2592342994E-03, 2.1205448461E-04, 1.8599202135E-07},
{1.2592342994E-03, 2.1205448461E-04, 1.8599202135E-07},
{1.2592342994E-03, 2.1205448461E-04, 1.8599202135E-07},
{1.2592342994E-03, 2.1205448461E-04, 1.8599202135E-07},
{1.2592342994E-03, 2.1205448461E-04, 1.8599202135E-07},
{1.2592342994E-03, 2.1205448461E-04, 1.8599202135E-07},
};

float arrayA[] = {C[0][0], C[1][0], C[2][0], C[3][0], C[4][0], C[5][0], C[6][0], C[7][0], C[8][0], C[9][0], C[10][0], C[11][0], C[12][0], C[13][0], C[14][0], C[15][0]};         // declare array and store values for coefficient A
float arrayB[] = {C[0][1], C[1][1], C[2][1], C[3][1], C[4][1], C[5][1], C[6][1], C[7][1], C[8][1], C[9][1], C[10][1], C[11][1], C[12][1], C[13][1], C[14][1], C[15][1]};         // declare array and store values for coefficient B
float arrayC[] = {C[0][2], C[1][2], C[2][2], C[3][2], C[4][2], C[5][2], C[6][2], C[7][2], C[8][2], C[9][2], C[10][2], C[11][2], C[12][2], C[13][2], C[14][2], C[15][2]};         // declare array and store values for coefficient C

int samples[NUMSAMPLES];           // define vector for sampling purpose of the thermistor() function  
float arrayV[16];                  // define array to store values of all probes before Serial print 
float arrayR[16];                  // define array to store resistances of all probes before Serial print
float arrayH[16];                  // define array to store humidities of all couples before Serial print

float R_wire[] = {0, 0, 0, 0, 0, 0, 0, 0, 0, 0, 0, 0, 0, 0, 0, 0};         // define array to store the extension wire values

String str;                            // define str in the general scope of the program
long readCycle2 = 0;                   // initialization of tag for live data (read function) (long type allows a high count values)
#define THERMISTORPIN A0               // Analog signals from all thermistors are multiplexed to a single pin
#define S0 2                           // Digital Pin 2 // Multiplexer #1 is controlled by 4 I/O pins
#define S1 3                           // Digital Pin 3 // Multiplexer #1 is controlled by 4 I/O pins
#define S2 4                           // Digital Pin 4 // Multiplexer #1 is controlled by 4 I/O pins   
#define S3 5                           // Digital Pin 5 // Multiplexer #1 is controlled by 4 I/O pins
struct STRUCT1 {float o; float t; };   // define a new structure class called 'STRUCT1 that will enable the thermistor function
struct STRUCT2 {float a;};               // define a new structure class called 'STRUCT2 that will enable the relhum function
unsigned long timePassed;              //initialize variable to keep track of time passed between each measurement
void(* resetFunc) (void) = 0;            // define a reset function for the arduino micro-controller

////// SETUP ////////
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

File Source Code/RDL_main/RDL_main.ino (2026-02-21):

/* RESISTANCE DATA LOGGER (RDL) SOURCE CODE
   Copyright (c) 2024 Jericho Laboratory Inc.

  THIS SOFTWARE IS PROVIDED BY THE COPYRIGHT HOLDERS AND CONTRIBUTORS "AS IS" AND ANY EXPRESS OR IMPLIED WARRANTIES, INCLUDING, BUT NOT LIMITED TO, THE
  IMPLIED WARRANTIES OF MERCHANTABILITY AND FITNESS FOR A PARTICULAR PURPOSE ARE DISCLAIMED. IN NO EVENT SHALL THE COPYRIGHT OWNER OR CONTRIBUTORS BE
  LIABLE FOR ANY DIRECT, INDIRECT, INCIDENTAL, SPECIAL, EXEMPLARY, OR CONSEQUENTIAL DAMAGES (INCLUDING, BUT NOT LIMITED TO, PROCUREMENT OF
  SUBSTITUTE GOODS OR SERVICES; LOSS OF USE, DATA, OR PROFITS; OR BUSINESS INTERRUPTION) HOWEVER CAUSED AND ON ANY THEORY OF LIABILITY, WHETHER IN
  CONTRACT, STRICT LIABILITY, OR TORT (INCLUDING NEGLIGENCE OR OTHERWISE) ARISING IN ANY WAY OUT OF THE USE OF THIS SOFTWARE, EVEN IF ADVISED OF THE
  POSSIBILITY OF SUCH DAMAGE. */

////////// USER PARAMETERS ////////////

bool headerDisplay = 1;                 // optional display of headerprint (1 = yes, 0 = no)
bool timeDisplay = 1;                   // optional display of timestamp (1 = yes, 0 = no)
bool idDisplay = 1;                     // optional display of identification number of measurement (1 = yes, 0 = no)
bool tDisplay = 1;                      // optional measurement and display of temperature/illuminance values (1 = yes, 0 = no)
bool ohmDisplay = 0;                    // optional display of probes resistance values (ohm) (1 = yes, 0 = no)
bool SHT40Display = 1;                  // optional measurement and display of i2c sensor values (1 = yes, 0 = no)
bool voltDisplay = 0;                   // optional measurement and display of voltage reading values (1 = yes, 0 = no)
bool currentDisplay = 0;                // optional measurement and display of True RMS current values (1 = yes, 0 = no)
bool terosDisplay = 1;                  // optional measurement and display of Teros 10 meter reading values (soil humidity) (1 = yes, 0 = no)
bool strainDisplay = 0;                 // optional measurement and display of strain gauge cell values (1 = yes, 0 = no)
bool phDisplay = 0;                     // optional measurement and display of pH meter values (1 = yes, 0 = no)
bool ControlSignal = 0;                 // optional activation of the signal control functions
bool periodicHeader = 1;                // optional activation of a printed header every given interval
bool currentTComp = 1;                  // optional activation of a temperature compensation on the current sensors (1 = yes, 0 = no)
bool dstRegion = 1;                     // define if you are in area where DST (Daylight Saving Time) is applied (1), or not (0).
bool T_readMode = 0;                    // readMode ==0 (Nano ADC) and readMode == 1 (ADS1115 ADC)
int i2cChannels_sht40[] = {8};          // define array to store the list of shield channels dedicated to air humidity sensors (channels 1 to 8)
int i2cChannels_strain[] = {1};         // define array to store the list of shield channels dedicated to strain sensors  (channels 1 to 8)
int i2cChannels_ph[] = {2};             // define array to store the list of shield channels dedicated to pH sensors  (channels 1 to 8)
int i2cChannels_current[] = {1,2,3};        // define array to store the list of analog channels dedicated to current sensors (channels 0 to 7)
int channels_teros[] = {0};           // define array to store the list of analog channels dedicated to TEROS sensors (channels 0 to 7)

////////// PROGRAMMER PARAMETERS ////////////

#define headerInterval 1800000          // (ms) Interval at which the header (sensors identification and units) is printed out (1800000 = 30min)  
#define Seriesresistor 10000            // (ohms) the value of the series resistor for T1 (based on the specifications of your RDL unit)
#define baudRate 57600                  // (bps) data rate at which data is transmitted between the Arduino and the PC, through the serial monitor (max = 115200)
#define ADCrange 65535                  // value range for 16-bit ADC (ADC1115) is 0-65535
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

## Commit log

2022-08-08 Initial commit of the whole project
    [BOM_RDL_revD6.csv, RDL_revD6-B_Cu.gbr, RDL_revD6-B_Mask.gbr, RDL_revD6-B_Paste.gbr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]
2022-08-23 Major update of application notes and also added BoM
    [BOM_RDL_RevD6.xlsx, jericho-coefficients-database.csv]
2022-08-31 soilFunc improved and other minor improvements
    tab 'soilDisplay.ino' was renamed 'soilFunc.ino' for coherence.
    soilFunc now can activate/deactivate temperature compensation.
    printerHeader now calls a String instead of modifying twice the printed text
2023-03-10 Replace AM2301 with SHT40 sensor
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2023-06-08 Fix the strain device integration
    Strain measurements were deactivated due to bad interaction with the SHT40/TCA9548. This is now fixed.
2023-06-09 Integrate TEROS 10 sensor to code
    Also a few corrections here and there
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2023-06-09 Fixing the stackoverflow by hanging sampling Hall
    Hall sensor used to have a large sampling vector to later do RMS value. This was changed to rolling sum .
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2023-08-27 Continued adaptation of code to brd Rev_E1
    - Create variable for 'enable' pin of A_MUX and T_MUX
    - Create adaptable header columns for voltages (V1 to V8)
    - Change name of RMS_func() to current_func()
    - Separate qty of voltage channels from thermistor channels
    - Remove printing of pH temperature
    - Fix readInterval display on startmessage (not updating)
    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
2024-01-08 Partial Developments
    Many partial developments.
    Code currently does not work.
    Branch RevE2 abandoned to pursue RevE3.
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2024-01-15 Improving code
    This code seems to work but it has a few bugs (stack overflow, probably after 17 lines, causes by SHT40). We are right before I try to MUX the strain sensor.
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2024-02-21 SHT40 Stack Overflow 2nd Correction
    After reevaluation, Else() and second if() were the true cause of the stack overflow. (which mostly happens when a channel is active but a SHT sensor cannot be found.
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2024-03-02 Rename PCB Design/RDL_revD6.kicad_pcb to PCB Design/old generation/RDL_revD6.kicad_pcb
    [RDL_revD6.kicad_pcb]
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2024-03-02 Rename PCB Design/RDL_revD6.kicad_pro.dsn to PCB Design/old generation/RDL_revD6.kicad_pro.dsn
    [RDL_revD6.kicad_pro.dsn]
2024-03-02 Rename PCB Design/RDL_revD6.kicad_sch to PCB Design/old generation/RDL_revD6.kicad_sch
    [RDL_revD6.kicad_sch]
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2024-03-04 Update I2C bus release strategy for SHT40
    SHT40: Adding tca_init() before cutting power to the MUX channel avoids the I2C bus jam even for 30m CAT cable. This is a great improvement. Delays have also been added to improve odds (effect not an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
2024-03-04 Update pH integration
    After verification, pH works in the main RJ45 but does not work with MUX. Most likely because both pH and MUX use the Wire.beginTransmission() statement. We will fix this in the near future.
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2024-03-20 Change of folder
    Changed the folder
    [RDL_revD6.kicad_pcb, RDL_revD6.kicad_pro.dsn, RDL_revD6.kicad_sch]
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2024-04-04 Delete Bill of Material directory
    In the future BoM can be found in /PCB Design folder along with other JLCPCB production files
    [BOM_RDL_RevD6.xlsx]
2024-04-15 Revert "Update Design Overview - Hall Effect Current Sensor.md"
    This reverts commit 6b13d49b5094f1fc889f931371df9bcf953b1d76.
2024-04-15 Revert "Update Design Overview - IP Camera System.md"
    This reverts commit 030f383963c4bf70e68250a6ecf72a2af7411dc2.
2024-04-15 Revert "Update Design Overview - Atmospheric Humidity Sensor.md"
    This reverts commit 6fbbc4e0166ed0085e5721f4cf768cd6cb077e38.
2024-04-20 Add 3D model ir-cam-adapter to documentation
    [camera_holder_v10.3mf, camera_holder_v10.FCStd, camera_holder_v10.f3d, camera_holder_v10.stl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]
2024-04-20 Add 3D model ice-bath-device to documentation
    [ice-bath-device-revB4-Body.stl, ice-bath-device-revB4.FCStd]
2024-04-21 Add 3D model of grid-for-SBC-fan to documentation
    [Grid-for-SBC-Fan.STL]
2024-04-21 Add 3D Model - Radiation Shield and Hub Bracket
    [PipeSupport.stl, Plates.3mf, Plates.stl, SensorSupport.3mf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]
2024-04-21 Add SHT4x_revA3 PCB design to documentation
    SHT4x is the more generic designation to the project since the chip is not always the SHT40 anymore.
    [BOM-WIRED_SHT40_revA3.csv, CPL-WIRED_SHT40_revA3.csv, WIRED_SHT40_revA3-CuBottom.gbr, WIRED_SHT40_revA3-CuTop.gbr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]
2024-04-21 Add NAU7802_revB1 PCB design to documentation
    [BOM-WIRED-NAU7802-board-revB1.csv, CPL-WIRED-NAU7802-board-revB1.csv, WIRED-NAU7802-board-revB1-CuBottom.gbr, WIRED-NAU7802-board-revB1-CuTop.gbr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]
2024-04-21 Cleanup the PCB Design folder
    [BOM_RDL_revD6.csv, RDL_revD6-B_Cu.gbr, RDL_revD6-B_Mask.gbr, RDL_revD6-B_Paste.gbr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]
2024-04-21 Add I2C-Shield-revA4 PCB design to documentation
    [BOM-WIRED-I2C-Shield-revA4.csv, CPL-WIRED-I2C-Shield-revA4.csv, WIRED-I2C-Shield-revA4-CuBottom.gbr, WIRED-I2C-Shield-revA4-CuTop.gbr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]
2024-04-21 Add pH-EZO-Carrier-revA1 PCB design to documentation
    [BOM-WIRED-pH-EZO-Carrier-revA1.csv, CPL-WIRED-pH-EZO-Carrier-revA1.csv, WIRED-pH-EZO-Carrier-revA1-CuBottom.gbr, WIRED-pH-EZO-Carrier-revA1-CuTop.gbr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]
2024-04-21 Correct folder name mistake
    [BOM_RDL_revD6.csv, RDL_revD6-B_Cu.gbr, RDL_revD6-B_Mask.gbr, RDL_revD6-B_Paste.gbr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]
2024-04-21 Add RDL_RevE4 PCB Design to Documentation
    [BOM-RDL_revE4.csv, CPL-RDL_revE4.csv, RDL_revE4-CuBottom.gbr, RDL_revE4-CuTop.gbr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]
2024-04-21 Create oldGen folder and add missing pdf SHT4x
    [BOM_RDL_revD6.csv, RDL_revD6-B_Cu.gbr, RDL_revD6-B_Mask.gbr, RDL_revD6-B_Paste.gbr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]
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2024-05-02 Fix thermal camera buffer problem
    Other minor modifications
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2024-06-23 Create first version of thermal camera carrier board revA1
    [BOM-WIRED-Seek-Board-revA1.csv, CPL-WIRED-Seek-Board-revA1.csv, WIRED-Seek-Board-revA1-CuBottom.gbr, WIRED-Seek-Board-revA1-CuTop.gbr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]
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2024-06-27 Minor corrections on currentNAU7802 function
2024-06-28 Trying to fix strain mux (WIP)
    Also added new headers for current function
2024-07-11 Adapt scripts and daemons to from Orange to RPI
    New content successfully tested on Raspberry
    Include the seekcamera-python wrapper.
    Remove old file.
    [E05257B12B1E-2024-07-11_114125.csv]
2024-08-01 Update allows basic mux for strain NAU7802
    Addition of enable(true) and enable(false) statements to put the nau7802 sensor into power down mode, which allows to revive the sensor at each loop without a new begin() statement , which caused mem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
2024-08-03 Fix basic reading Current-NAU7802 (still Sparkfun)
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2024-08-05 Making progress towards MUX
    It seems to works now with a single MUXED current sensor. But the first reading after hot plug is wrong.
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2024-08-14 Fix current sensor behavior (partial fix)
    enable(default) was called even if the current sensor was absent. This provoked reset.
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2024-09-02 Clean accidental files
    [E05257B12B1E-2024-07-11_114125.csv]
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2024-11-05 Add timeout value to Serial comms (i2c jams)
    Added a timeout to the definition of Serial port. This allows getting out of readline() when i2c bus jams. Eventually, the jam_threshold is reached and scripts stops via break statement. Service rest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
    Also add timestamp to error message.
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2025-03-08 Correct excessive new lines print out
    Serial.println() statement was outside the sensor-read block, causing the serial monitor to print a great amount of new lines as the main loop cycles.
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2025-04-03 Added support for multiple strain gauge cell
    Transfer strain calibration values out of the function.
    Arduino code now reads strain calibration values from header file (.h).
    Created Excel file containing calibration procedure and calib values.
    New Python script (runMe.py) that creates calibration header file from Excel file.
    Add moment value display and adjust printed header.
    [coefficients_source.xlsx]
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2025-04-14 Apply rounding function for coefficients (xls)
    [coefficients_source.xlsx]
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2025-05-08 Add temperature compensation to current sensor
    Dummy values replaced with real values based on exp 2025-05-03-Freezer. Large improvement on reliability of current sensor across large temperature span (-10 to +40C). Highly linear relationship.
    Also, some old comments removed and other minor corrections.
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2025-05-08 Print out clear dummy values when problem with current sensor
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2025-08-11 Minor changes like filename updates
    [coefficients_source.xlsx, coefficients_source_strain.xlsx]
2025-08-11 Add coefficient library for current sensor calibration
    current_coefficients.h
    Other minor corrections and cleaning
2025-08-21 Complete redesign of syncing.py
    Complete redesign of WIRED-syncing.py to solve syncing issues:
    - false syncing of files while internet is down
    - files uploaded to wrong cloud path (e.g. truncated path)
    Per-file pipeline:
    1) Upload local file to a temp path on Dropbox: /<relpath>.tmp_<rand>
    2) Round-trip download and SHA-256 verify against local
    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

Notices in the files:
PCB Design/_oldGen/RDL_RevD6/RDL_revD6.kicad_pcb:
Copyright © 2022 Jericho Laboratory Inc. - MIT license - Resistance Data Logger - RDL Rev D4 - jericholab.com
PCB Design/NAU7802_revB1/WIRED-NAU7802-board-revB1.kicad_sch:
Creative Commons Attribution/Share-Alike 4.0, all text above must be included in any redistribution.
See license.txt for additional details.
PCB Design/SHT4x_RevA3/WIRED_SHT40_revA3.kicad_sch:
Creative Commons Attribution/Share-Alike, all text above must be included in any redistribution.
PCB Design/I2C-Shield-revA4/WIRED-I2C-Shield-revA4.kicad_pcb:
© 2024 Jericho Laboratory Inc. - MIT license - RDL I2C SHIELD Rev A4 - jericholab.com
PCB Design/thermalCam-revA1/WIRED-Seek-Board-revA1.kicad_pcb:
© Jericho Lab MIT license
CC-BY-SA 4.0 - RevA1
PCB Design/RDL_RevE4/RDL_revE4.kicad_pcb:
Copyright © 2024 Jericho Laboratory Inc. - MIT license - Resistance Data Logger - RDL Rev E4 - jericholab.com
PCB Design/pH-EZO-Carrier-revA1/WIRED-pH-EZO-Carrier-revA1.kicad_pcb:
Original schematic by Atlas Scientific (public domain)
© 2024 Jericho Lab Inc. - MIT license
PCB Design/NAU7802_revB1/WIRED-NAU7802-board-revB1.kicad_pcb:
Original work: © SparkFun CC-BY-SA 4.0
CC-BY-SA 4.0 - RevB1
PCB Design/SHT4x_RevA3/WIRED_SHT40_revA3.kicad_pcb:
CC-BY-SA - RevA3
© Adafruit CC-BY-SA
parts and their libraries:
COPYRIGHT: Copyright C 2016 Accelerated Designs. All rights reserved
